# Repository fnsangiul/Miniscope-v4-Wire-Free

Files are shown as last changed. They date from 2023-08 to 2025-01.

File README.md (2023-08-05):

# Miniscope-v4-Wire-Free

The Miniscope v4 Wire-Free is an open-source one photon miniatirized microscope for neural recordings in freely behaving animals.  

<p align="center">
  
</p>

This microscope is based on the Miniscope v4, sharing the same optical properties with redesigned electronics. This repository contains the KiCAD project files for the electronics, the complete microcontroller project and the Jupyter notebooks used to set the recording parameters and recover the data from the SD card.

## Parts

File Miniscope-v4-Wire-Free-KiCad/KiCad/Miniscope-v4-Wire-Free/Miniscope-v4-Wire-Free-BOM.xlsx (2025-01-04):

Item | Quantity | Reference(s) | Value | Description | Manufacturer Name | Manufacturer Part Number
1 | 9 | C1, C2, C6, C7, C26, C35, C50, C51, C52 | 10uF | CAP CER 10UF 6.3V X5R 0402 | Murata | GRM155R60J106ME15D
2 | 2 | C3, C4 | 10pF | CAP CER 10PF 50V C0G/NP0 0201 | Murata | GRM0335C1H100FA01J
3 | 5 | C5, C11, C12, C13, C15 | 2.2uF | CAP CER 2.2UF 10V X5R 0201 | Murata | GRM033R61A225KE47D
4 | 22 | C9, C10, C19, C22, C23, C24, C25, C27, C28, C30, C38, C40, C41, C42, C43, C44, C45, C46, C47, C48, C49, C53 | 0.1uF | CAP CER 0.1UF 25V X5R 0201 | Murata | GRM033R61E104KE14J
5 | 2 | C14, C37 | 1uF | CAP CER 1UF 10V X5R 0201 | Murata | GRM033R61A105ME15D
6 | 1 | C16 | 4.7nF 100V | CAP CER 4700PF 100V X7R 0603 | Murata | GCM188R72A472KA37D
7 | 3 | C17, C29, C36 | 4.7uF | CAP CER 4.7UF 6.3V X5R 0201 | Murata | GRM035R60J475ME15D
8 | 2 | C18, C20 | 22pF | CAP CER 22PF 50V C0G/NP0 0201 | Murata | GRM0335C1H220GA01D
9 | 1 | D1 | LXZ1-PB01 | LED LUXEON Z BLUE 470NM SMD | Lumileds | LXZ1-PB01
10 | 2 | D2,D3 | RED LED | LED RED CLEAR THIN 0603 SMD | Lite-On Inc. | LTST-C191KEKT
11 | 1 | J1 | 475710001 | CONN MICRO SD CARD PUSH-PULL R/A | Molex | 475710001
12 | 2 | L1, L5 | 10uH | FIXED IND 10UH 300MA 600MOHM SMD | TDK | MLZ1608N100LT000
13 | 1 | L2 | 4.7uH | FIXED IND 4.7UH 180MA 300MOHM SM | Abracon | ASMCI-0805-4R7M-T
14 | 2 | L3, L4 | BLM18PG471SN1D | FERRITE BEAD 470 OHM 0603 1LN | Murata | BLM18PG471SN1D
15 | 1 | Q1 | NTK3134NT1G | Power MOSFET | ON Semiconductor | NTK3134NT1G
16 | 1 | Q2 | MMBT3904LP-7B | TRANS NPN 40V 0.2A DFN1006-3 | Diodes Incorporated | MMBT3904LP-7B
17 | 2 | R1, R17 | 25K | RES SMD 24.9K OHM 1% 1/20W 0201 | Vishay Dale | CRCW020124K9FNED
18 | 2 | R2, R18 | 1.8K | RES SMD 1.8K OHM 1% 1/20W 0201 | Panasonic | ERJ-1GNF1801C
19 | 1 | R3 | 1.25M | RES 1.27M OHM 1% 1/20W 0201 | Vishay Dale | CRCW02011M27FNED
20 | 1 | R4 | 2.05M | RES 2.05M OHM 1% 1/20W 0201 | Vishay Dale | CRCW02012M05FNED
21 | 1 | R5 | 1M | RES SMD 1M OHM 1% 1/20W 0201 | Vishay Dale | CRCW02011M00FNED
22 | 1 | R6 | 649K | RES SMD 649K OHM 1% 1/20W 0201 | Vishay Dale | CRCW0201649KFNED
23 | 2 | R7, R8 | 2.2K | RES SMD 2.2K OHM 1% 1/20W 0201 | Panasonic | ERJ-1GNF2201C
24 | 1 | R9 | 8.2K | RES SMD 8.2K OHM 1% 1/20W 0201 | Vishay Dale | CRCW02018K20FKED
25 | 1 | R10 | 2K | RES SMD 2K OHM 1% 1/20W 0201 | Vishay Dale | CRCW02012K00FNED
26 | 2 | R11, R19 | 1K | RES SMD 1K OHM 1% 1/20W 0201 | Vishay Dale | CRCW02011K00FKED
27 | 1 | R12 | DNL | DNL | DNL | DNL
28 | 1 | R13 | 400K | RES SMD 402K OHM 1% 1/20W 0201 | Panasonic | ERJ-1GNF4023C
29 | 3 | R14, R16, R20 | 100K | RES SMD 100K OHM 1% 1/20W 0201 | Panasonic | ERJ-1GNF1003C
30 | 1 | R15 | 37K | RES SMD 37.4K OHM 1% 1/20W 0201 | Panasonic | ERJ-1GNF3742C
31 | 1 | R21 | 47k5 | RES SMD 47.5K OHM 1% 1/20W 0201 | Vishay Dale | CRCW020147K5FNED
32 | 1 | R22 | 10K | RES SMD 10K OHM 1% 1/20W 0201 | Vishay Dale | ERJ-1GNF1002C
33 | 1 | SW1 | TL3780AF330QG | SWITCH TACTILE SPST-NO 0.02A 15V | E-Switch | TL3780AF330QG
34 | 1 | U1 | LTC3554 | IC USB POWER MANAGER 20UTQFN | Analog Devices Inc. | LTC3554EUD#PBF
35 | 1 | U2 | HV892 | IC LED DRIVER LENS 10WDFN | Microchip | HV892K7-G
36 | 1 | U3 | LTC3218 | IC LED DRIVER RGLTR 150MA 10DFN | Analog Devices Inc. | LTC3218
37 | 1 | U4 | MAX13030EETE+BGA | IC TRNSLTR BIDIRECTIONAL 16TQFN | Maxim Integrated | MAX13030EETE+
38 | 1 | U5 | TSOP57438TT1 | SENSOR REMOTE REC 38.0KHZ 40M | Vishay Semiconductor Opto Division | TSOP57438TT1
39 | 1 | U6 | ATSAMD51J20A-UUT-EFP | MCU 120MHZ 1024KB FLASH 64 | Microchip | ATSAMD51J20A-UUT-EFP
40 | 1 | U7 | NCP163AMX330TBG | IC REG LINEAR 3.3V 250MA 4XDFN | onsemi | NCP163AMX330TBG
41 | 1 | U8 | NOIP1SN0480A | IC CMOS IMAGE SENSOR 1/3.6" | onsemi | NOIP1SN0480A-STI1
42 | 1 | U9 | LMV321IDCKR | IC OPAMP GP 1 CIRCUIT SC70-5 | Texas Instruments | LMV321IDCKR
43 | 1 | J3 | FH19C-4S-0.5SH | CONN FFC BOTTOM 4POS 0.5MM R/A | Hirose | FH19C-4S-0.5SH(10)
44 | 1 | Y2 | Crystal | CRYSTAL 32.7680KHZ 12.5PF SMD | TXC CORPORATION | 9HT11-32.768KBZF-T
Total | 91

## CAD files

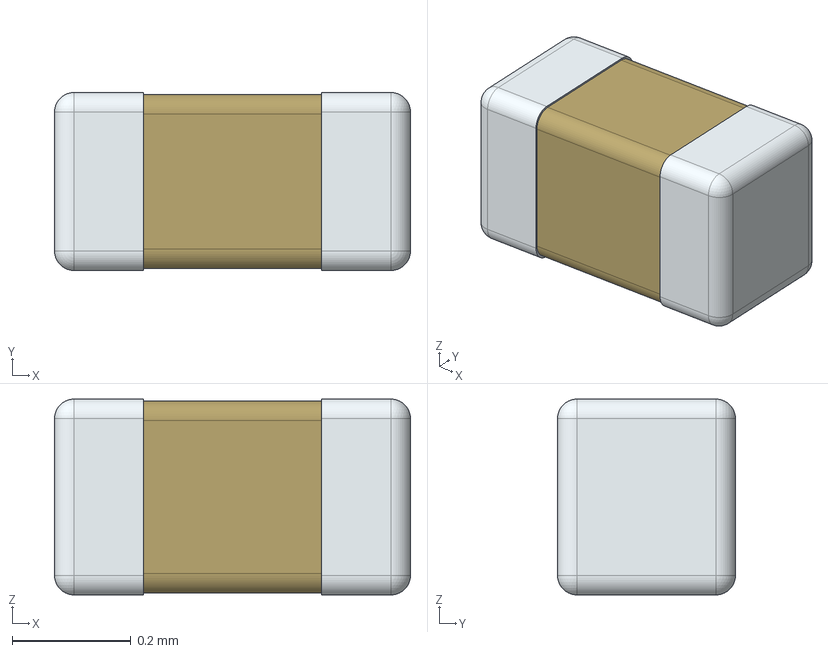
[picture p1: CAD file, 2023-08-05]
Miniscope-v4-Wire-Free-KiCad/KiCad/Miniscope-v4-Wire-Free/3D Models/GRM033R61A105ME15D.stp
0.6 x 0.3 x 0.33 mm

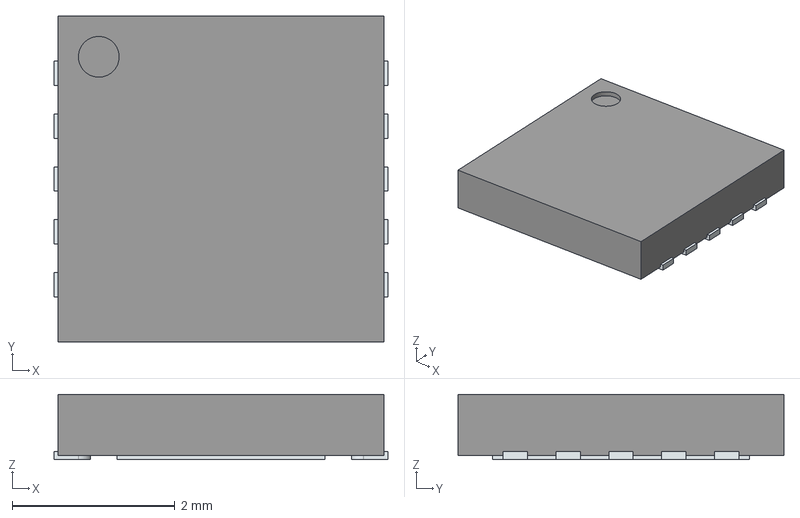
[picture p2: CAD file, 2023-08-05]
Miniscope-v4-Wire-Free-KiCad/KiCad/Miniscope-v4-Wire-Free/3D Models/HV892K7-G.stp
4.10 x 4.00 x 0.8 mm
ThermalPin
PinsArrayLR

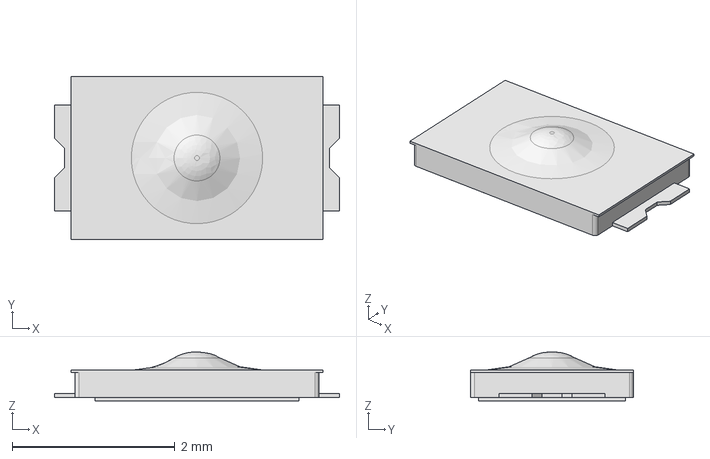
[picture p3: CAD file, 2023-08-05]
Miniscope-v4-Wire-Free-KiCad/KiCad/Miniscope-v4-Wire-Free/3D Models/TL3780AFxxxQG.stp
3.50 x 2.00 x 0.6 mm

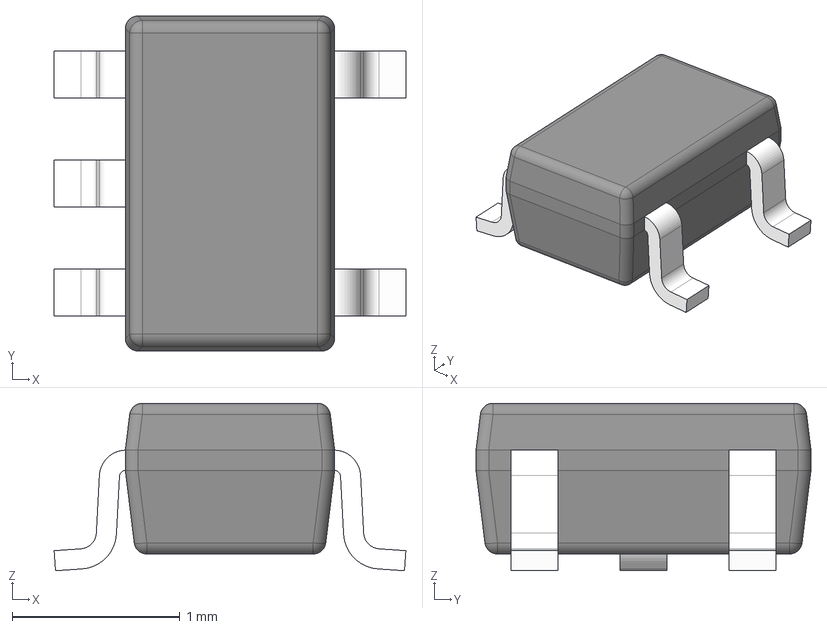
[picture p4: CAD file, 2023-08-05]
Miniscope-v4-Wire-Free-KiCad/KiCad/Miniscope-v4-Wire-Free/3D Models/LMV321IDCKR.stp
2.10 x 2.00 x 1.00 mm
BODY-SOT
LEAD-SOT x 5
PIN1-ID

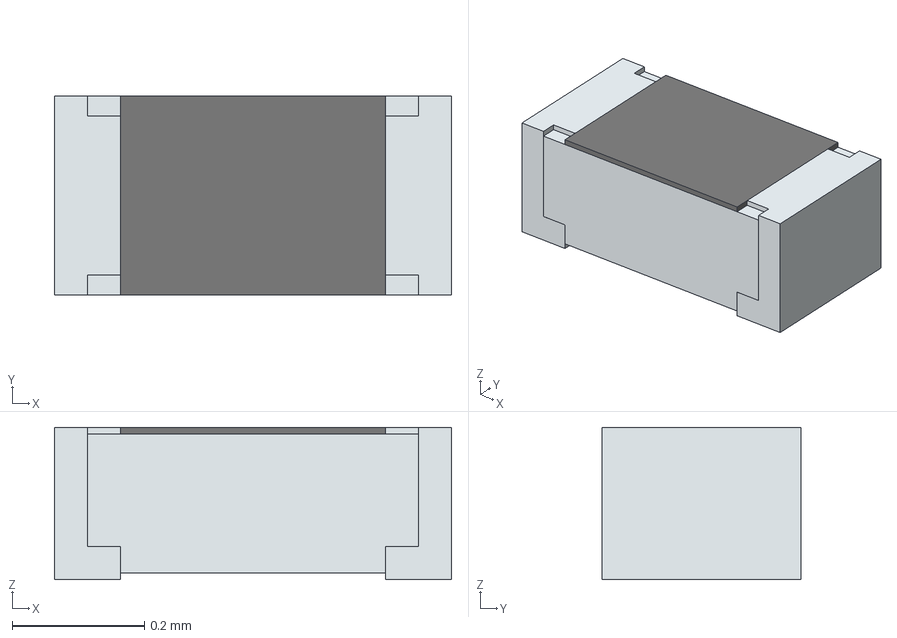
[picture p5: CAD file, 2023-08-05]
Miniscope-v4-Wire-Free-KiCad/KiCad/Miniscope-v4-Wire-Free/3D Models/ERJ-1GNF4023C.stp
0.6 x 0.3 x 0.23 mm
solidBody
Terminal
solidTop

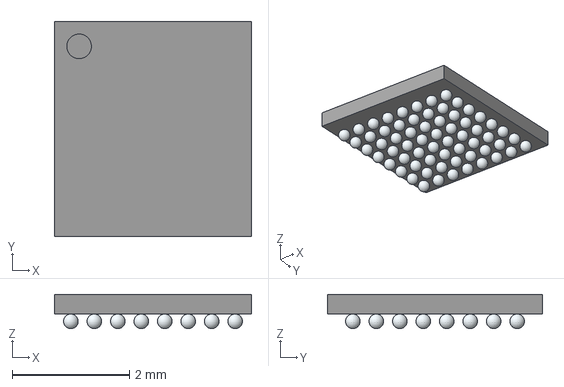
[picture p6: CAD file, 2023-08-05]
Miniscope-v4-Wire-Free-KiCad/KiCad/Miniscope-v4-Wire-Free/3D Models/STM32L451REY6TR.stp
3.36 x 3.66 x 0.585 mm

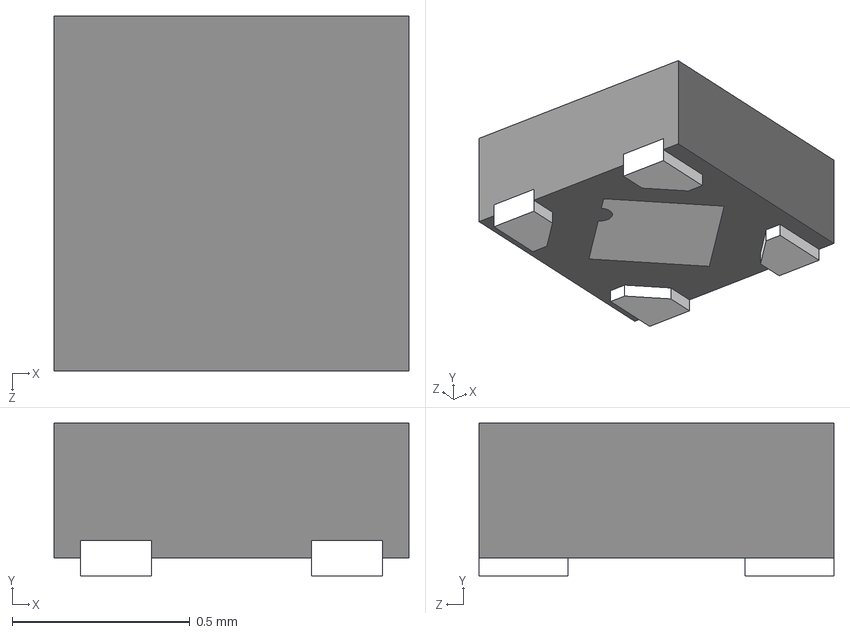
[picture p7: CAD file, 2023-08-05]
Miniscope-v4-Wire-Free-KiCad/KiCad/Miniscope-v4-Wire-Free/3D Models/NCP163AMX180TBG.stp
1.00 x 0.43 x 1.00 mm

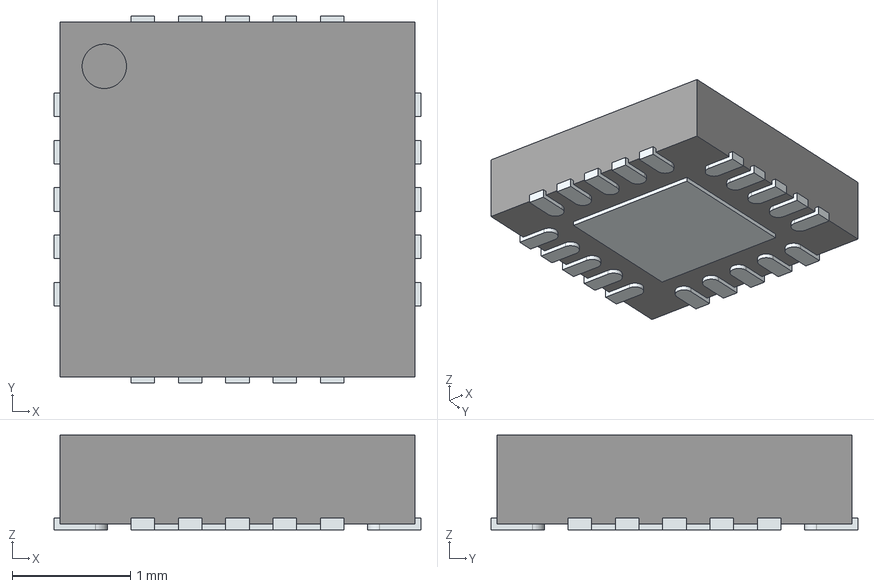
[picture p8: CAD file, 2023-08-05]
Miniscope-v4-Wire-Free-KiCad/KiCad/Miniscope-v4-Wire-Free/3D Models/LTC3554EUD-3#PBF.stp
3.10 x 3.10 x 0.8 mm
ThermalPin
PinsArrayLR
PinsArrayTB

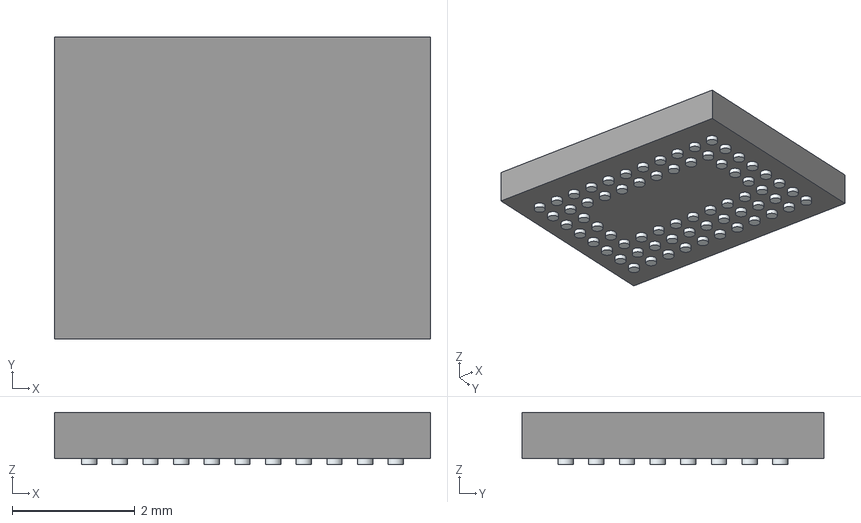
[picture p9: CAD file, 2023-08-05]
Miniscope-v4-Wire-Free-KiCad/KiCad/Miniscope-v4-Wire-Free/3D Models/NOIP1SP0480A-STI.stp
6.13 x 4.93 x 0.85 mm
Pins

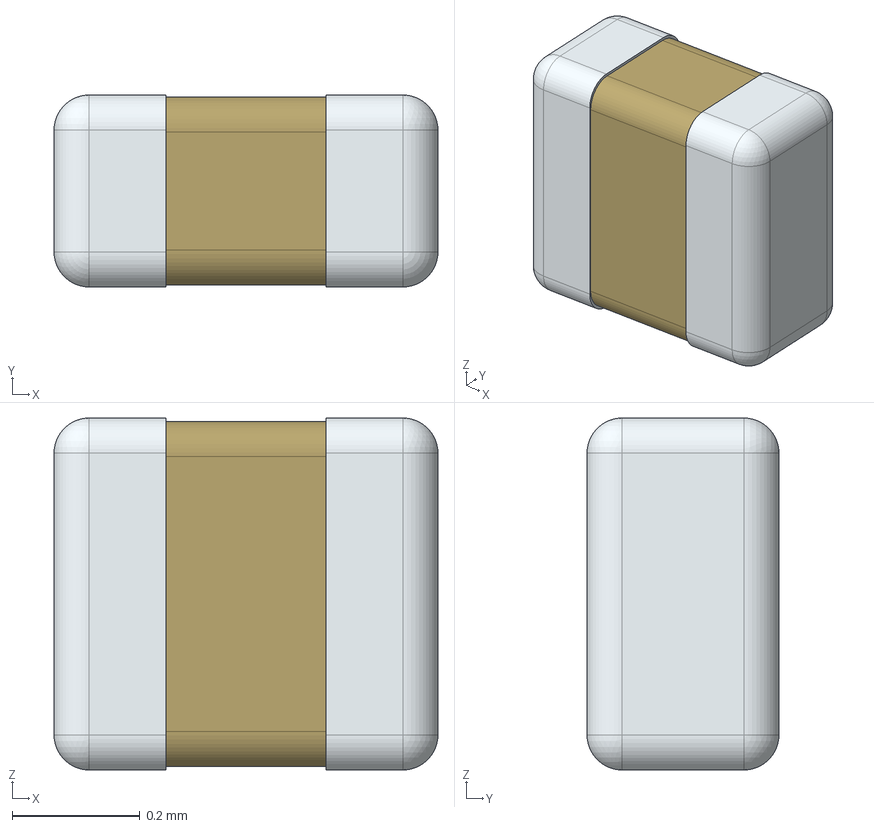
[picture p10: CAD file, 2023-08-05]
Miniscope-v4-Wire-Free-KiCad/KiCad/Miniscope-v4-Wire-Free/3D Models/GRM035R60J475ME15D.stp
0.6 x 0.3 x 0.55 mm

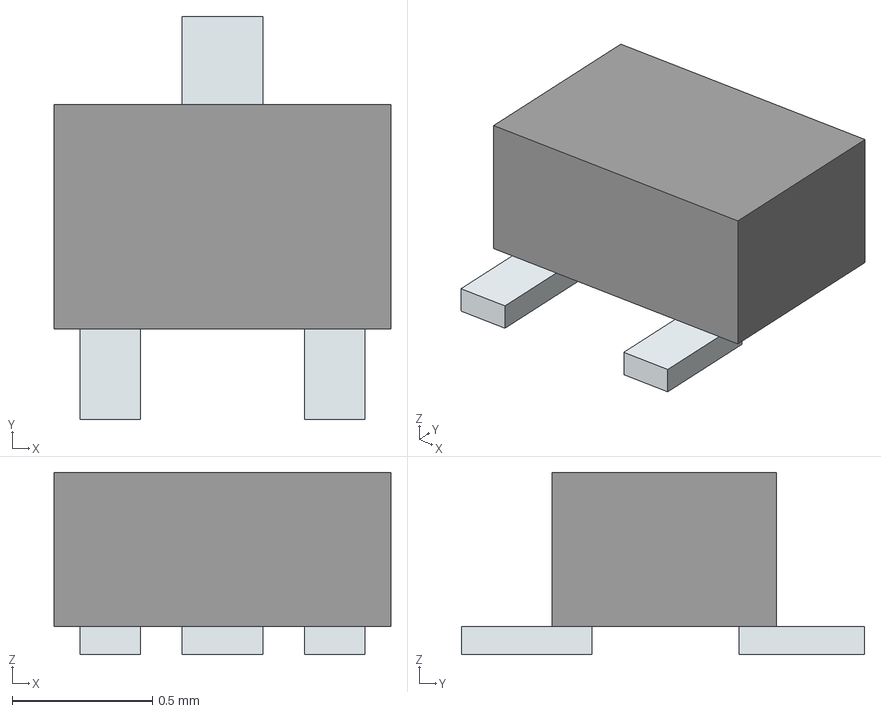
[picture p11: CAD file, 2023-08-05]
Miniscope-v4-Wire-Free-KiCad/KiCad/Miniscope-v4-Wire-Free/3D Models/NTK3134NT1G.stp
1.20 x 1.44 x 0.65 mm
Pins

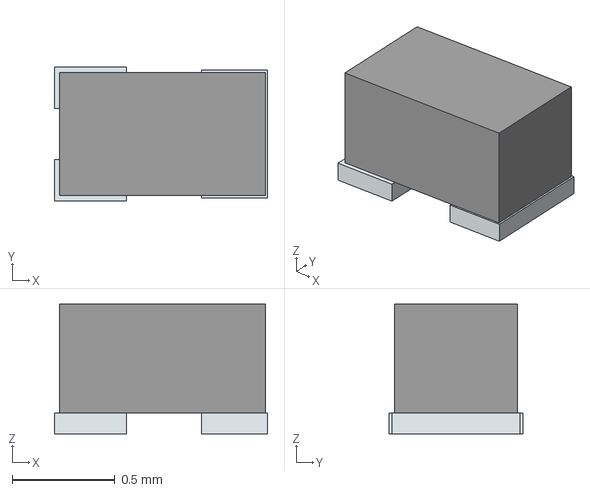
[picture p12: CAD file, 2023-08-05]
Miniscope-v4-Wire-Free-KiCad/KiCad/Miniscope-v4-Wire-Free/3D Models/MMBT3904LP-7B.stp
1.04 x 0.65 x 0.63 mm
Pins

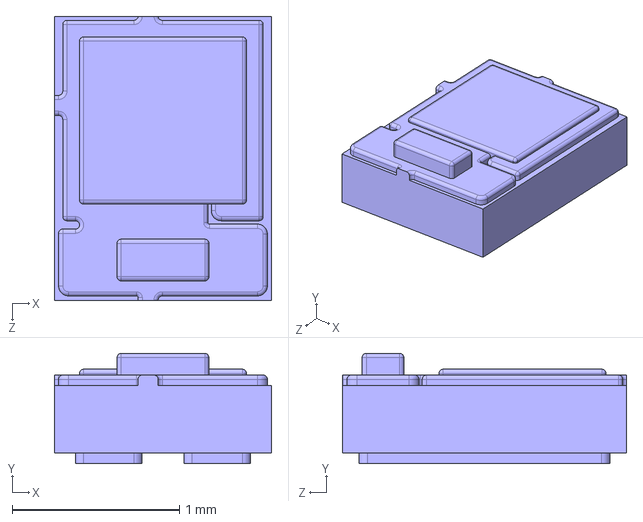
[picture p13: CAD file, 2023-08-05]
Miniscope-v4-Wire-Free-KiCad/KiCad/Miniscope-v4-Wire-Free/3D Models/LXZ1-PB01.stp
1.30 x 0.66 x 1.70 mm

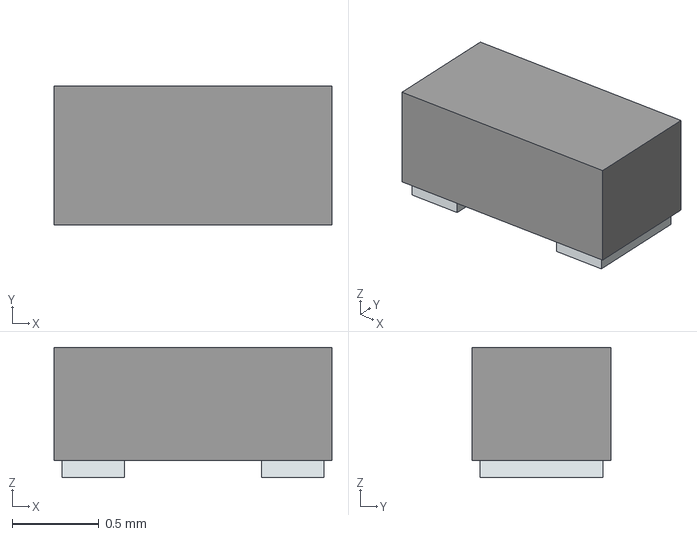
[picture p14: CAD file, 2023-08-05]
Miniscope-v4-Wire-Free-KiCad/KiCad/Miniscope-v4-Wire-Free/3D Models/LTST-C191KEKT.stp
1.60 x 0.8 x 0.75 mm
Pins

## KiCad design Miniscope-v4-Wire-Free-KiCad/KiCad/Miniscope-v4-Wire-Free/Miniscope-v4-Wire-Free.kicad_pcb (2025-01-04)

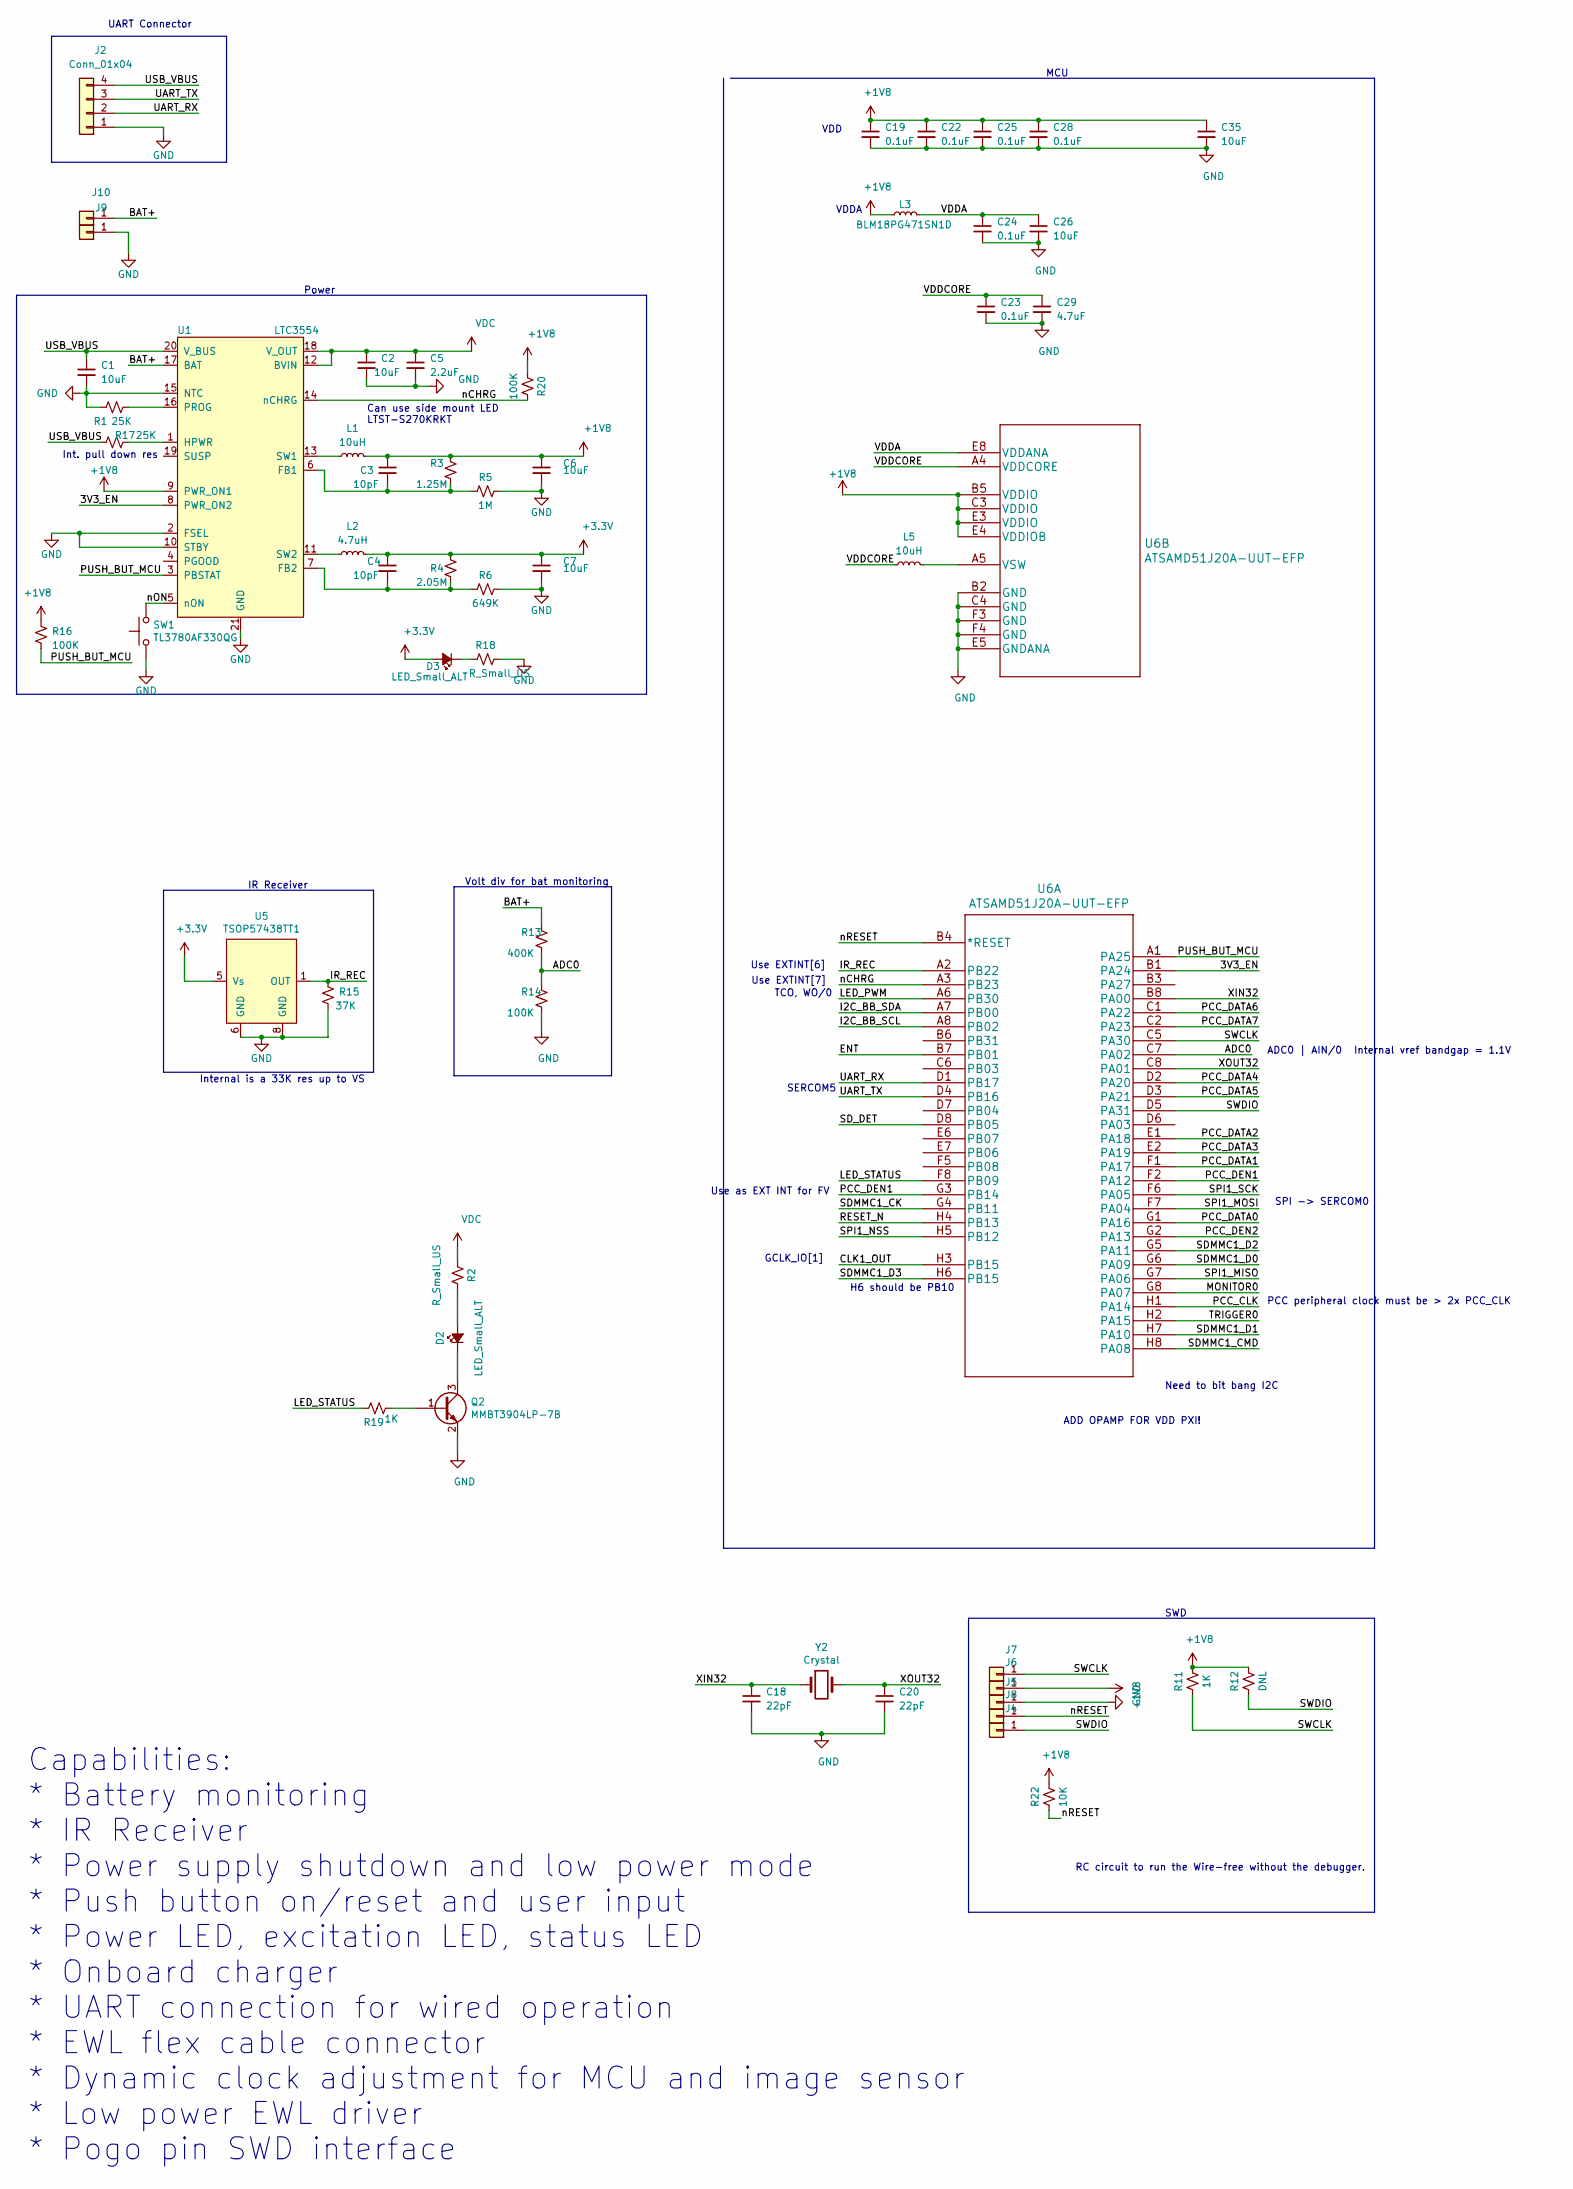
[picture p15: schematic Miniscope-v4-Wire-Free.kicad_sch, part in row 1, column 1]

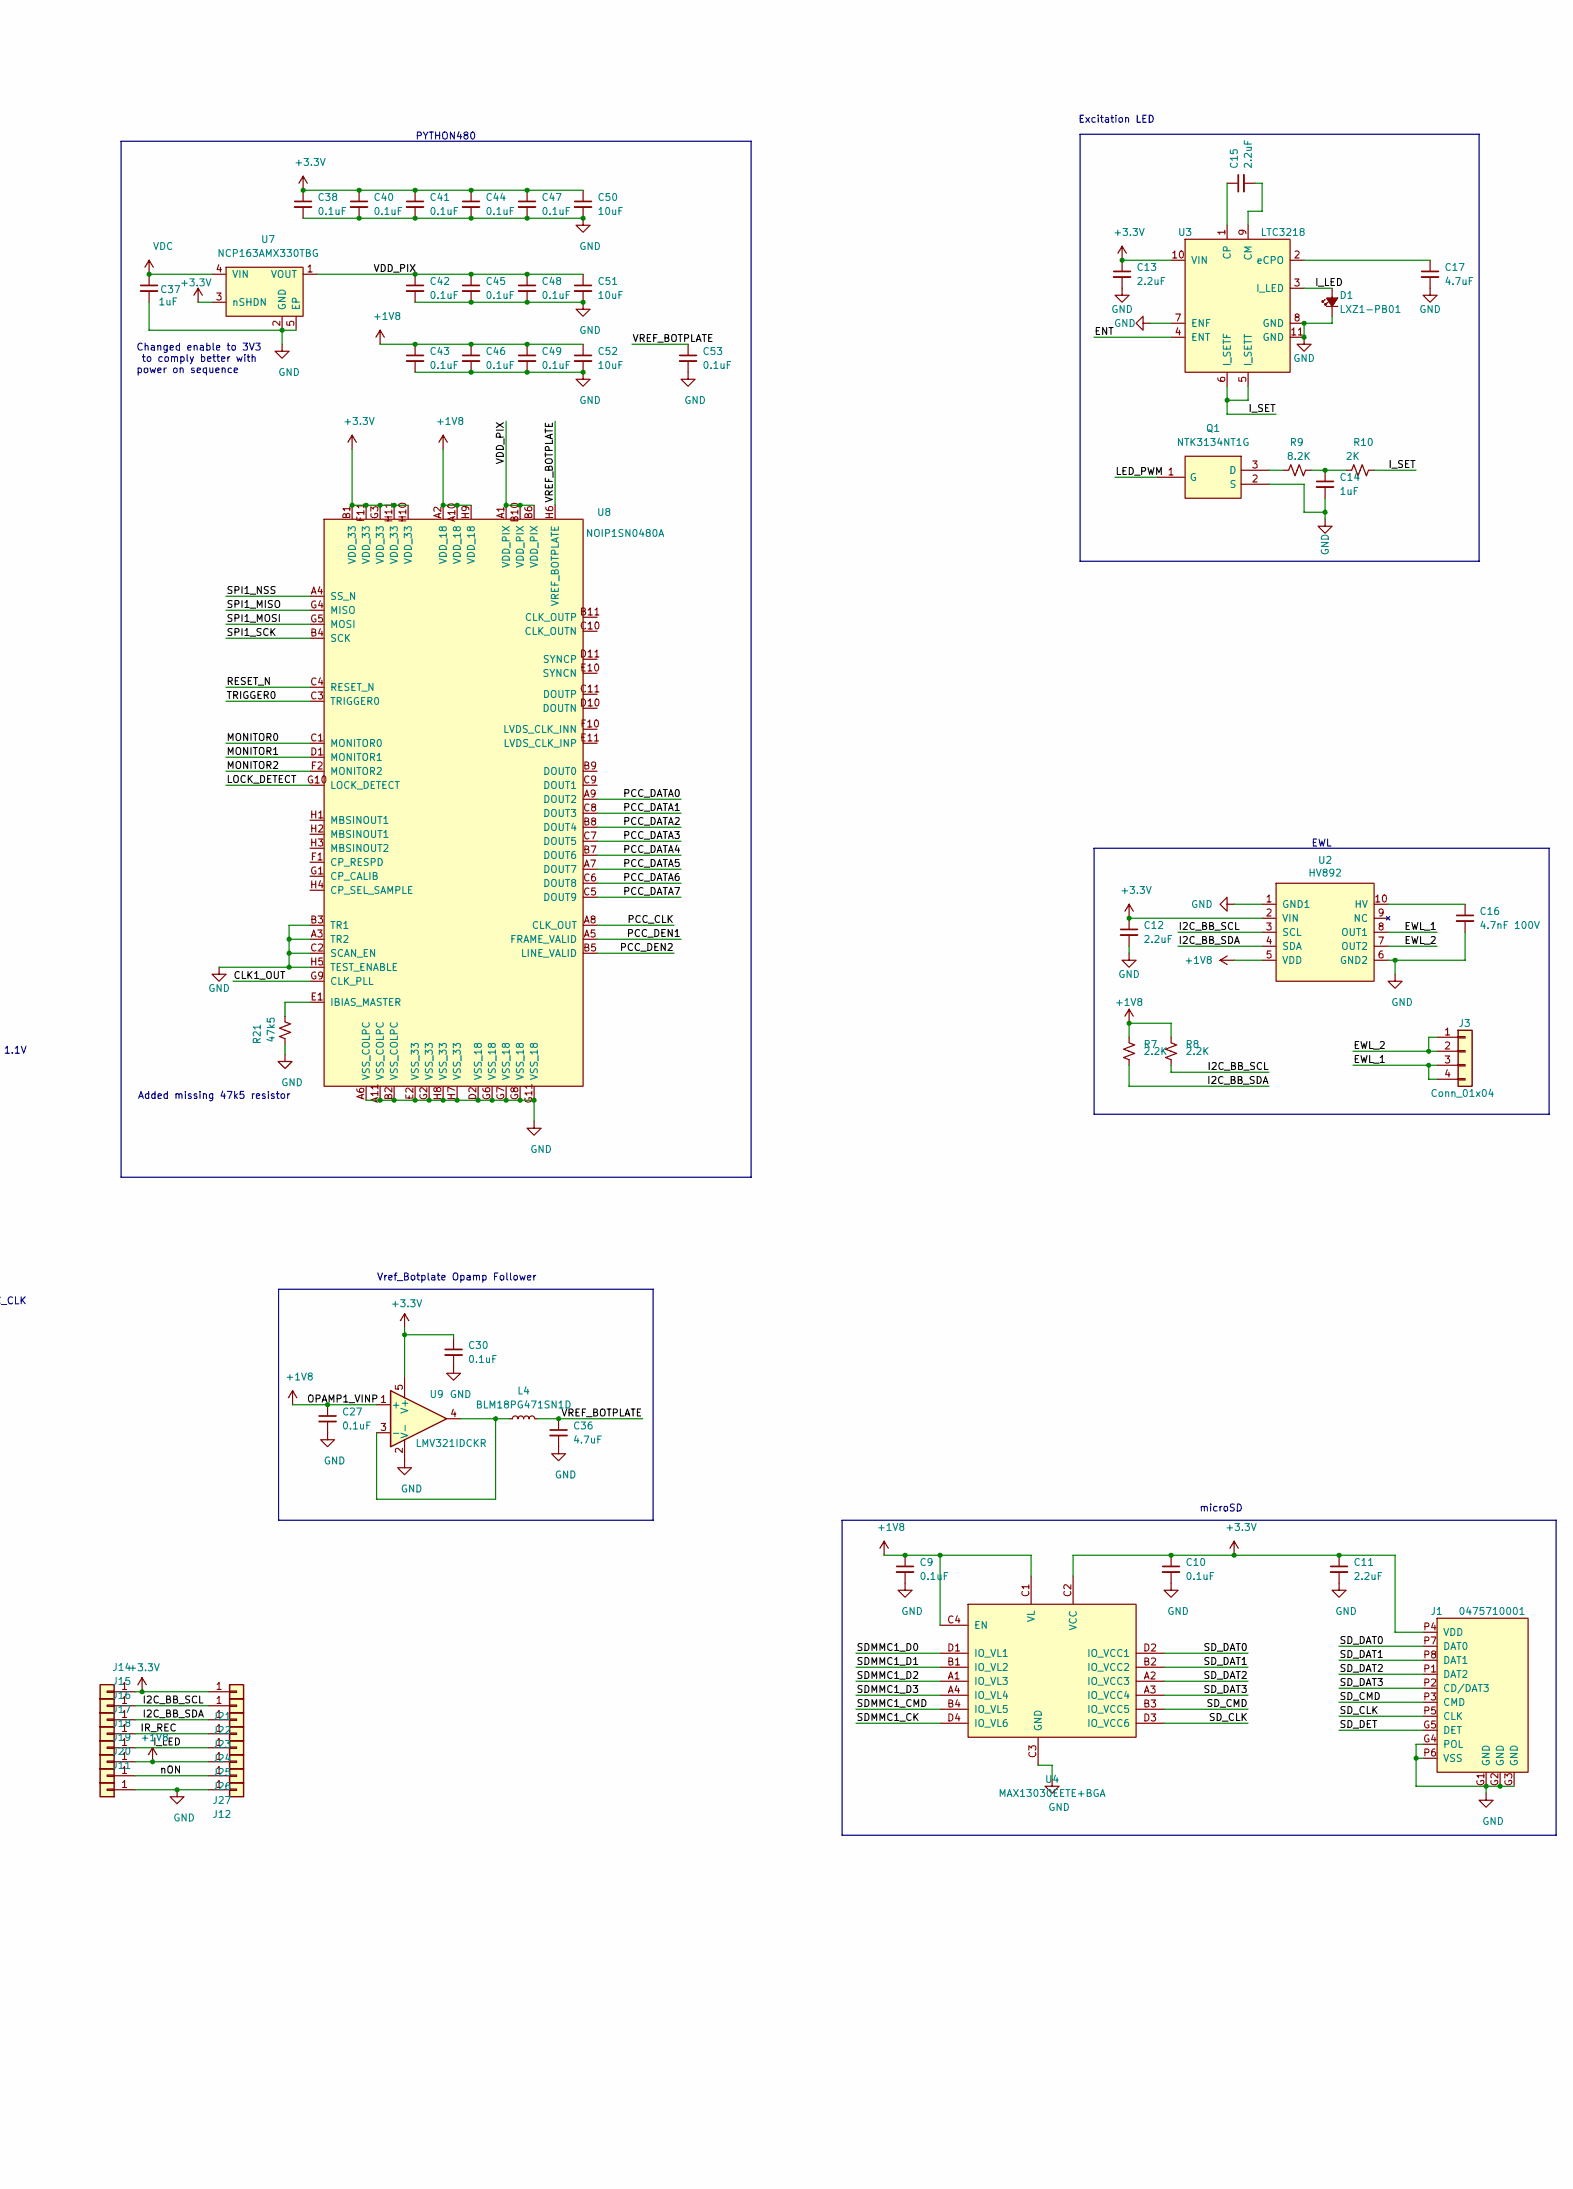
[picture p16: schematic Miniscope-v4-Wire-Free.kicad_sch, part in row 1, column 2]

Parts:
C1, C2, C6, C7, C26, C35, C50, C51, C52: 10uF; C_0402_1005Metric_L; Manufacturer_Part_Number GRM155R60J106ME15D
C3, C4: 10pF; C_0201_0603Metric_L; Manufacturer_Part_Number GRM0335C1H100FA01J
C5, C11, C12, C13, C15: 2.2uF; C_0201_0603Metric_L; Manufacturer_Part_Number GRM033R61A225KE47D
C9, C10, C19, C22, C23, C24, C25, C27, C28, C30, C38, C40, C41, C42, C43, C44, C45, C46, C47, C48, C49, C53: 0.1uF; C_0201_0603Metric_L; Manufacturer_Part_Number GRM033R61E104KE14J
C14, C37: 1uF; C_0201_0603Metric_L; Manufacturer_Part_Number GRM033R61A105ME15D
C16: 4.7nF 100V; C_0603_1608Metric_L; Manufacturer_Part_Number GCM188R72A472KA37D
C17, C29, C36: 4.7uF; C_0201_0603Metric_L; Manufacturer_Part_Number GRM035R60J475ME15D
C18, C20: 22pF; C_0201_0603Metric_L; Manufacturer_Part_Number GRM0335C1H220GA01D
D1: LXZ1-PB01; LED_LXZ1_PR01_L; Manufacturer_Part_Number LXZ1-PB01
D2, D3: LED_Small_ALT; LED_SC80X160X65L40L
J1: 0475710001; Manufacturer_Part_Number 0475710001
J2: Conn_01x04; 1x4_USB; Manufacturer_Part_Number DNL
J3: Conn_01x04; FH19C-4S-0.5SH(10); Manufacturer_Part_Number DNL
J4, J5, J6, J7, J8, J9, J10, J11, J12, J14, J15, J16, J17, J18, J19, J20, J21, J22, J23, J24, J25, J26, J27: Conn_01x01; Conn_1x1_700_Circular_Pad; Manufacturer_Part_Number DNL
L1, L5: 10uH; C_0805_2012Metric_L; Manufacturer_Part_Number MLZ1608N100LT000
L2: 4.7uH; C_0805_2012Metric_L; Manufacturer_Part_Number ASMCI-0805-4R7M-T
L3, L4: BLM18PG471SN1D; L_0603_1608Metric_L; Manufacturer_Part_Number BLM18PG471SN1D
Q1: NTK3134NT1G; TRXSOFL3P40_120X120X55L29X21L; Manufacturer_Part_Number NTK3134NT1G; Mouser Part Number 863-NTK3134NT1G
Q2: MMBT3904LP-7B; TRXDFN3_101X61X53L25X15N; Manufacturer_Part_Number MMBT3904LP-7B
R1, R17: 25K; R_0201_0603Metric_ERJ_L; Manufacturer_Part_Number CRCW020124K9FNED
R2, R18: R_Small_US; R_0201_0603Metric_ERJ_L
R3: 1.25M; R_0201_0603Metric_ERJ_L; Manufacturer_Part_Number CRCW02011M27FNED
R4: 2.05M; R_0201_0603Metric_ERJ_L; Manufacturer_Part_Number CRCW02012M05FNED
R5: 1M; R_0201_0603Metric_ERJ_L; Manufacturer_Part_Number CRCW02011M00FNED
R6: 649K; R_0201_0603Metric_ERJ_L; Manufacturer_Part_Number CRCW0201649KFNED
R7, R8: 2.2K; R_0201_0603Metric_ERJ_L; Manufacturer_Part_Number ERJ-1GNF2201C
R9: 8.2K; R_0201_0603Metric_ERJ_L; Manufacturer_Part_Number CRCW02018K20FKED
R10: 2K; R_0201_0603Metric_ERJ_L; Manufacturer_Part_Number CRCW02012K00FNED
R11, R19: 1K; R_0201_0603Metric_ERJ_L; Manufacturer_Part_Number CRCW02011K00FKED
R12: DNL; R_0201_0603Metric_ERJ_L; Manufacturer_Part_Number DNL
R13: 400K; R_0201_0603Metric_ERJ_L; Manufacturer_Part_Number ERJ-1GNF4023C
R14, R16, R20: 100K; R_0201_0603Metric_ERJ_L; Manufacturer_Part_Number ERJ-1GNF1003C
R15: 37K; R_0201_0603Metric_ERJ_L; Manufacturer_Part_Number ERJ-1GNF3742C
R21: 47k5; R_0201_0603Metric_ERJ_L; Manufacturer_Part_Number CRCW020147K5FNED
R22: 10K; R_0201_0603Metric_ERJ_L; Manufacturer_Part_Number CRCW02011K00FKED
SW1: TL3780AF330QG; SMD-Switch-3mmx2mm; Manufacturer_Part_Number TL3780AF330QG
U1: LTC3554; QFN-20-1EP_3x3mm_P0.4mm_EP1.65x1.65mm; Manufacturer_Part_Number LTC3554EUD#PBF
U2: HV892; SON11P65_400X400X80L40X30T315X255L; Manufacturer_Part_Number HV892K7-G
U3: LTC3218; SON_11_P50_300X200X80L40X25T239X64L; Manufacturer_Part_Number LTC3218
U4: MAX13030EETE+BGA; BGA-16_1.92x1.92mm_Layout4x4_P0.5mm; Manufacturer_Part_Number MAX13030EETE+
U5: TSOP57438TT1; SON_4_P300_395X395X90L55X35L; Manufacturer_Part_Number TSOP57438TT1
U6: ATSAMD51J20A-UUT-EFP; Manufacturer_Part_Number ATSAMD51J20A-UUT-EFP
U7: NCP163AMX330TBG; UQFN_MCP1711; Manufacturer_Part_Number NCP163AMX330TBG
U8: NOIP1SN0480A; BGA88CP50_8X11_493X613X75B25; Manufacturer_Part_Number NOIP1SN0480A-STI1
U9: LMV321IDCKR; SOT_23-5P65_210X110L36X22L
Y2: Crystal; Crystal_SMD_MicroCrystal_CC8V-T1A-2Pin_2.0x1.2mm

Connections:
+1V8: C3.1, C6.1, C9.1, C19.1, C22.1, C25.1, C27.1, C28.1, C35.1, C43.1, C46.1, C49.1, C52.1, J6.1, J19.1, J26.1, L1.2, L3.1, R3.1, R7.1, R8.1, R11.1, R12.1, R16.1, R20.2, R22.1, U1.9 (PWR_ON1), U2.5 (VDD), U4.C1 (VL), U4.C4 (EN), U6.B5 (VDDIO), U6.C3 (VDDIO), U6.E3 (VDDIO), U6.E4 (VDDIOB), U8.A2 (VDD_18), U8.A10 (VDD_18), U8.H9 (VDD_18), U9.1 (+)
+3V3: C4.1, C7.1, C10.1, C11.1, C12.1, C13.1, C30.1, C38.1, C40.1, C41.1, C44.1, C47.1, C50.1, D3.2 (A), J1.P4 (VDD), J14.1, J21.1, L2.2, R4.1, U2.2 (VIN), U3.10 (VIN), U4.C2 (VCC), U5.5 (Vs), U7.3 (nSHDN), U8.B1 (VDD_33), U8.F11 (VDD_33), U8.G3 (VDD_33), U8.H10 (VDD_33), U8.H11 (VDD_33), U9.5 (V+)
/3V3_EN: U1.8 (PWR_ON2), U6.B1 (PA24)
/ADC0: R13.2, R14.1, U6.C7 (PA02)
/BAT+: J10.1, R13.1, U1.17 (BAT)
/CLK1_OUT: U6.H3 (PB15), U8.G9 (CLK_PLL)
/ENT: U3.4 (ENT), U6.B7 (PB01)
/EWL_1: J3.3, J3.4, U2.8 (OUT1)
/EWL_2: J3.1, J3.2, U2.7 (OUT2)
/I2C_BB_SCL: J15.1, J22.1, R8.2, U2.3 (SCL), U6.A8 (PB02)
/I2C_BB_SDA: J16.1, J23.1, R7.2, U2.4 (SDA), U6.A7 (PB00)
/IR_REC: J17.1, J24.1, R15.1, U5.1 (OUT), U6.A2 (PB22)
/I_LED: D1.A, J18.1, J25.1, U3.3 (I_LED)
/I_SET: R10.1, U3.5 (I_SETT), U3.6 (I_SETF)
/LED_PWM: Q1.1 (G), U6.A6 (PB30)
/LED_STATUS: R19.2, U6.F8 (PB09)
/LOCK_DETECT: U8.G10 (LOCK_DETECT)
/MONITOR0: U6.G8 (PA07), U8.C1 (MONITOR0)
/MONITOR1: U8.D1 (MONITOR1)
/MONITOR2: U8.F2 (MONITOR2)
/PCC_CLK: U6.H1 (PA14), U8.A8 (CLK_OUT)
/PCC_DATA0: U6.G1 (PA16), U8.A9 (DOUT2)
/PCC_DATA1: U6.F1 (PA17), U8.C8 (DOUT3)
/PCC_DATA2: U6.E1 (PA18), U8.B8 (DOUT4)
/PCC_DATA3: U6.E2 (PA19), U8.C7 (DOUT5)
/PCC_DATA4: U6.D2 (PA20), U8.B7 (DOUT6)
/PCC_DATA5: U6.D3 (PA21), U8.A7 (DOUT7)
/PCC_DATA6: U6.C1 (PA22), U8.C6 (DOUT8)
/PCC_DATA7: U6.C2 (PA23), U8.C5 (DOUT9)
/PCC_DEN1: U6.F2 (PA12), U6.G3 (PB14), U8.A5 (FRAME_VALID)
/PCC_DEN2: U6.G2 (PA13), U8.B5 (LINE_VALID)
/PUSH_BUT_MCU: R16.2, U1.3 (PBSTAT), U6.A1 (PA25)
/RESET_N: U6.H4 (PB13), U8.C4 (RESET_N)
/SDMMC1_CK: U4.D4 (IO_VL6), U6.G4 (PB11)
/SDMMC1_CMD: U4.B4 (IO_VL5), U6.H8 (PA08)
/SDMMC1_D0: U4.D1 (IO_VL1), U6.G6 (PA09)
/SDMMC1_D1: U4.B1 (IO_VL2), U6.H7 (PA10)
/SDMMC1_D2: U4.A1 (IO_VL3), U6.G5 (PA11)
/SDMMC1_D3: U4.A4 (IO_VL4), U6.H6 (PB15)
/SD_CLK: J1.P5 (CLK), U4.D3 (IO_VCC6)
/SD_CMD: J1.P3 (CMD), U4.B3 (IO_VCC5)
/SD_DAT0: J1.P7 (DAT0), U4.D2 (IO_VCC1)
/SD_DAT1: J1.P8 (DAT1), U4.B2 (IO_VCC2)
/SD_DAT2: J1.P1 (DAT2), U4.A2 (IO_VCC3)
/SD_DAT3: J1.P2 (CD/DAT3), U4.A3 (IO_VCC4)
/SD_DET: J1.G5 (DET), U6.D8 (PB05)
/SPI1_MISO: U6.G7 (PA06), U8.G4 (MISO)
/SPI1_MOSI: U6.F7 (PA04), U8.G5 (MOSI)
/SPI1_NSS: U6.H5 (PB12), U8.A4 (SS_N)
/SPI1_SCK: U6.F6 (PA05), U8.B4 (SCK)
/SWCLK: J7.1, R11.2, U6.C5 (PA30)
/SWDIO: J4.1, R12.2, U6.D5 (PA31)
/TRIGGER0: U6.H2 (PA15), U8.C3 (TRIGGER0)
/UART_RX: J2.2, U6.D1 (PB17)
/UART_TX: J2.3, U6.D4 (PB16)
/USB_VBUS: C1.1, J2.4, R17.2, U1.20 (V_BUS)
/VDDA: C24.1, C26.1, L3.2, U6.E8 (VDDANA)
/VDDCORE: C23.1, C29.1, L5.1, U6.A4 (VDDCORE)
/VDD_PIX: C42.1, C45.1, C48.1, C51.1, U7.1 (VOUT), U8.A1 (VDD_PIX), U8.B6 (VDD_PIX), U8.B10 (VDD_PIX)
/VREF_BOTPLATE: C36.1, C53.1, L4.2, U8.H6 (VREF_BOTPLATE)
/XIN32: C18.1, U6.B8 (PA00), Y2.1
/XOUT32: C20.1, U6.C8 (PA01), Y2.2
/nCHRG: R20.1, U1.14 (nCHRG), U6.A3 (PB23)
/nON: J20.1, J27.1, SW1.2, U1.5 (nON)
/nRESET: J8.1, R22.2, U6.B4 (*RESET)
GND: C1.2, C2.2, C5.2, C6.2, C7.2, C9.2, C10.2, C11.2, C12.2, C13.2, C14.2, C16.2, C17.2, C18.2, C19.2, C20.2, C22.2, C23.2, C24.2, C25.2, C26.2, C27.2, C28.2, C29.2, C30.2, C35.2, C36.2, C37.2, C38.2, C40.2, C41.2, C42.2, C43.2, C44.2, C45.2, C46.2, C47.2, C48.2, C49.2, C50.2, C51.2, C52.2, C53.2, D1.C, J1.G1 (GND), J1.G2 (GND), J1.G3 (GND), J1.G4 (POL), J1.P6 (VSS), J2.1, J5.1, J9.1, J11.1, J12.1, Q1.2 (S), Q2.2 (E), R1.2, R5.1, R6.1, R14.2, R15.2, R18.1, R21.2, SW1.1, U1.2 (FSEL), U1.10 (STBY), U1.15 (NTC), U1.21 (GND), U2.1 (GND1), U2.6 (GND2), U3.7 (ENF), U3.8 (GND), U3.11 (GND), U4.C3 (GND), U5.6 (GND), U5.8 (GND), U6.B2 (GND), U6.C4 (GND), U6.E5 (GNDANA), U6.F3 (GND), U6.F4 (GND), U7.2 (GND), U7.5 (EP), U8.A3 (TR2), U8.A6 (VSS_COLPC), U8.A11 (VSS_COLPC), U8.B2 (VSS_COLPC), U8.B3 (TR1), U8.C2 (SCAN_EN), U8.D2 (VSS_18), U8.E2 (VSS_33), U8.G2 (VSS_33), U8.G6 (VSS_18), U8.G7 (VSS_18), U8.G8 (VSS_18), U8.G11 (VSS_18), U8.H5 (TEST_ENABLE), U8.H7 (VSS_33), U8.H8 (VSS_33), U9.2 (V-)
unnamed: C14.1, R9.1, R10.2
unnamed: D2.2 (A), R2.1
unnamed: D2.1 (K), Q2.3 (C)
unnamed: D3.1 (K), R18.2
unnamed: Q1.3 (D), R9.2
unnamed: Q2.1 (B), R19.1
unnamed: C3.2, R3.2, R5.2, U1.6 (FB1)
unnamed: C4.2, R4.2, R6.2, U1.7 (FB2)
unnamed: R17.1, U1.1 (HPWR)
unnamed: R1.1, U1.16 (PROG)
unnamed: L1.1, U1.13 (SW1)
unnamed: L2.1, U1.11 (SW2)
unnamed: C16.1, U2.10 (HV)
unnamed: C15.2, U3.9 (CM)
unnamed: C15.1, U3.1 (CP)
unnamed: C17.1, U3.2 (eCPO)
unnamed: L5.2, U6.A5 (VSW)
unnamed: R21.1, U8.E1 (IBIAS_MASTER)
unnamed: L4.1, U9.3 (-), U9.4
VDC: C2.1, C5.1, C37.1, R2.2, U1.12 (BVIN), U1.18 (V_OUT), U7.4 (VIN)

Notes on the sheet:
UART Connector
IR Receiver
Use EXTINT[7]
Excitation LED
EWL
Changed enable to 3V3 to comply better with power on sequence
microSD
Int. pull down res
GCLK_IO[1]
Can use side mount LED LTST-S270KRKT
PYTHON480
Internal is a 33K res up to VS
Added missing 47k5 resistor
SPI -> SERCOM0
H6 should be PB10
Capabilities: * Battery monitoring * IR Receiver * Power supply shutdown and low power mode * Push button on/reset and user input * Power LED, excitation LED, status LED * Onboard charger * UART connection for wired operation * EWL flex cable connector * Dynamic clock adjustment for MCU and image s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
ADC0 | AIN/0
SERCOM5
Use EXTINT[6]
Need to bit bang I2C
Vref_Botplate Opamp Follower
VDD
SWD
Power
Use as EXT INT for FV
MCU
Volt div for bat monitoring
TCO, WO/0
VDDA
RC circuit to run the Wire-free without the debugger.
PCC peripheral clock must be > 2x PCC_CLK
ADD OPAMP FOR VDD PXI!
Internal vref bandgap = 1.1V

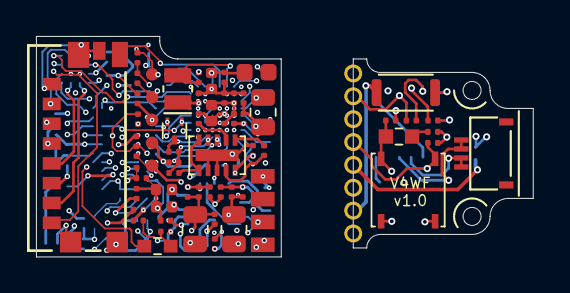
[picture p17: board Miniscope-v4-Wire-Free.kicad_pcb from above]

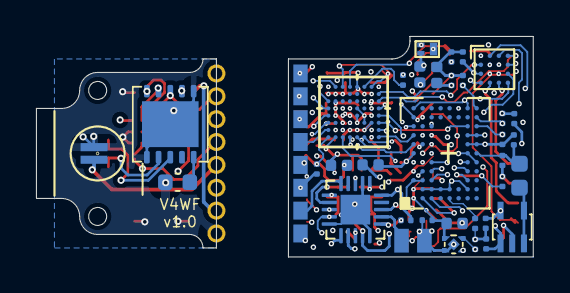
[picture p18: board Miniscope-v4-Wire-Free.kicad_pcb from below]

Board: 6 copper layers, 13.6 x 12.2 mm, 115 parts (44 on the bottom side), 83 nets.

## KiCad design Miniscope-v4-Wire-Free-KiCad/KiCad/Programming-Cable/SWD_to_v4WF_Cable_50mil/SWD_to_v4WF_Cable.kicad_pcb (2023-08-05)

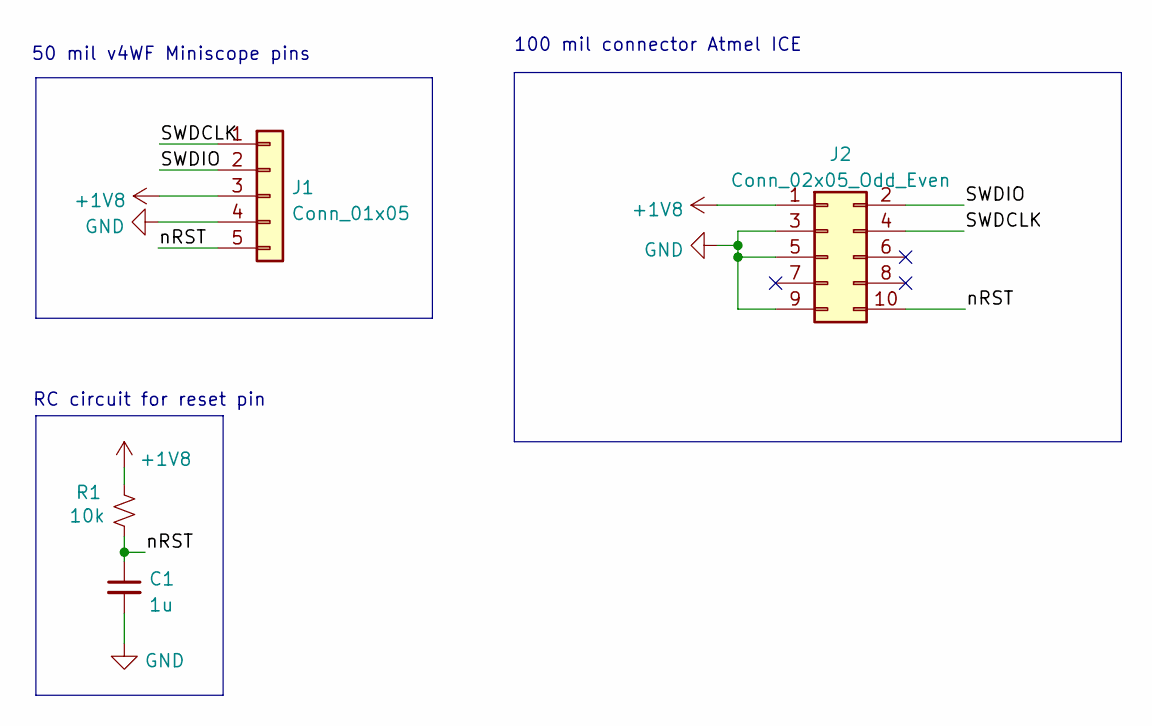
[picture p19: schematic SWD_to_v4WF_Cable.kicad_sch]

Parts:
C1: 1u; C_0805_2012Metric_Pad1.18x1.45mm_HandSolder
J1: Conn_01x05; PinSocket_1x05_P1.27mm_Vertical
J2: Conn_02x05_Odd_Even; PinHeader_2x05_P2.54mm_Horizontal
R1: 10k; R_0805_2012Metric_Pad1.20x1.40mm_HandSolder

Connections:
+1V8: J1.3, J2.1, R1.1
/SWDCLK: J1.1, J2.4
/SWDIO: J1.2, J2.2
/nRST: C1.1, J1.5, J2.10, R1.2
GND: C1.2, J1.4, J2.3, J2.5, J2.9

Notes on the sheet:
RC circuit for reset pin
50 mil v4WF Miniscope pins
100 mil connector Atmel ICE

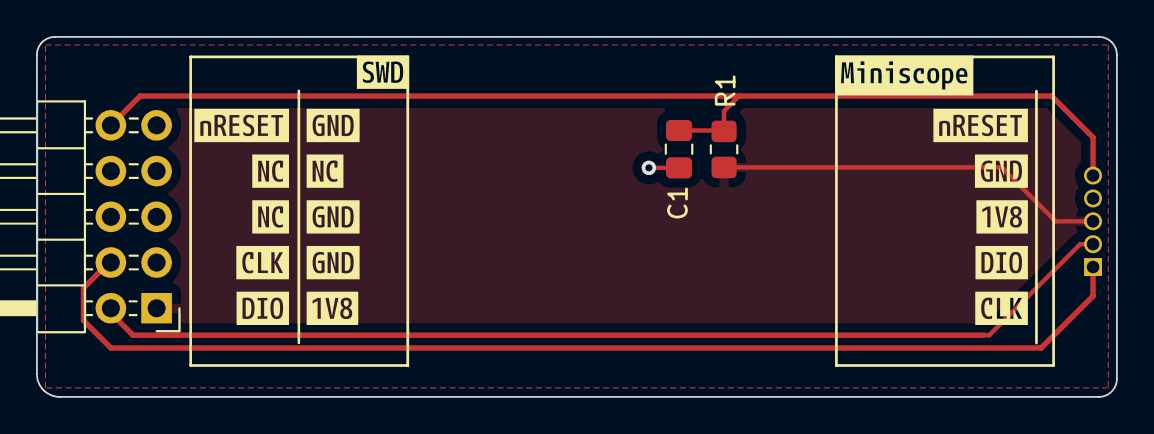
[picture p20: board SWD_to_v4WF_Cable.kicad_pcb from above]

Board: 2 copper layers, 60.0 x 20.0 mm, 21 parts (1 on the bottom side), 5 nets.

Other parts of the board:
kibuzzard-630EA2F1: G***; kibuzzard-630EA2F1
kibuzzard-630EA6B9: G***; kibuzzard-630EA6B9
kibuzzard-630EA6CF: G***; kibuzzard-630EA6CF
kibuzzard-630EA6DD: G***; kibuzzard-630EA6DD
kibuzzard-630EA6F1: G***; kibuzzard-630EA6F1
kibuzzard-630EA36E: G***; kibuzzard-630EA36E
kibuzzard-630EA39E: G***; kibuzzard-630EA39E
kibuzzard-630EA059: G***; kibuzzard-630EA059
kibuzzard-630EA251, kibuzzard-630EA251#2, kibuzzard-630EA251#3: G***; kibuzzard-630EA251
kibuzzard-630EA342, kibuzzard-630EA342#2, kibuzzard-630EA342#3: G***; kibuzzard-630EA342
kibuzzard-630EA384: G***; kibuzzard-630EA384
kibuzzard-630EA721: G***; kibuzzard-630EA721
kibuzzard-630EA733: G***; kibuzzard-630EA733

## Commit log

2023-08-05 Updates to the jupyter notebooks
    - Added capability to recover the timestamps from the recording and generate a comma separated value file
    - Added the pullup resistor to the reset line of the MCU in the PCB.
    - Added the gerbers used for the batch fabrication
    [475710001.stp, ERJ-1GNF4023C.stp, EWL_FlexPC-B_Cu.gbr, EWL_FlexPC-B_Mask.gbr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]
2025-01-04 Added new gerbers for the fabrication outputs for version 1.0
    - Generated new fabrication outputs for the v1.0
    - Corrected the resistor value for the reset pull up resistor (from 1k to 10k)
    [Miniscope-v4-Wire-Free-BOM.xlsx, Miniscope-v4-Wire-Free-B_Cu.gbr, Miniscope-v4-Wire-Free-B_Mask.gbr, Miniscope-v4-Wire-Free-B_Paste.gbr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]

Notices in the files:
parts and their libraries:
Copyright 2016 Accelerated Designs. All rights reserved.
